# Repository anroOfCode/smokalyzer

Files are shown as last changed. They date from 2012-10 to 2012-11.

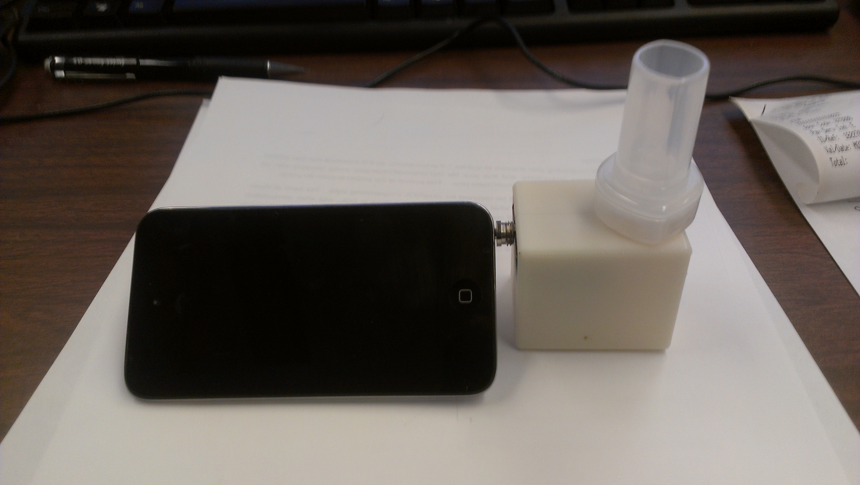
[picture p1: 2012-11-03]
photos/2012-10-05 15.16.02.jpg

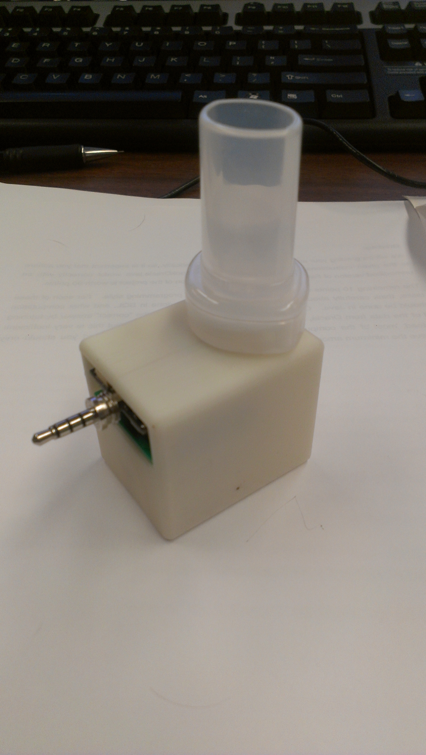
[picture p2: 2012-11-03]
photos/2012-10-05 15.00.42.jpg

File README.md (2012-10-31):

smokalyzer
==========
Code and design files for a headset-connected device that can detect if you've been smoking.

Info
====
This project is based on the HiJack platform. It includes an interface board designed for use with an electrochemical gas sensor, 3D design files for the creation of an enclosure, and code for iOS and for the HiJack platform that allows for reading and calibration.

What You'll Find Here
=====================

Code for Use With TinyOS
------------------------
Code has been written to be used with the HiJack platform, installed with TinyOS. TinyOS is difficult to setup, but the process should look something like this:

- Check out version 2.1.1 from the TinyOS Subversion page
- Install it on your local machine, including tos-tools. (see documentation on their site)
- Check out the hijack-main code from the google code project and copy the directory structure such that it matches up with your tinyos main folder
- Build the apps using 'make hijack install miniprog bsl,/dev/ttyUSB0'

An iOS App That Displays CO Data
--------------------------------
This is one of my very, very first endeavors into iOS app making. The code is not clean but will hopefully be cleaned up over time. We've imported libHiJack from the HiJack project as well, which requires delicacy when it comes to using ARC. The app supports basic calibration and reading of the instrument. 

Board Design Files
------------------
The files will allow you to order more of the PCB. They have been produced using Eagle 6.3.0.

Enclosure Design Files
----------------------
These files can serve as a starting point for a professional enclosure. They can also be 3D prototyped by any 3D lab for prototype enclosures. 

Questions?
==========
Feel free to contact me with questions. Responses are not guaranteed.

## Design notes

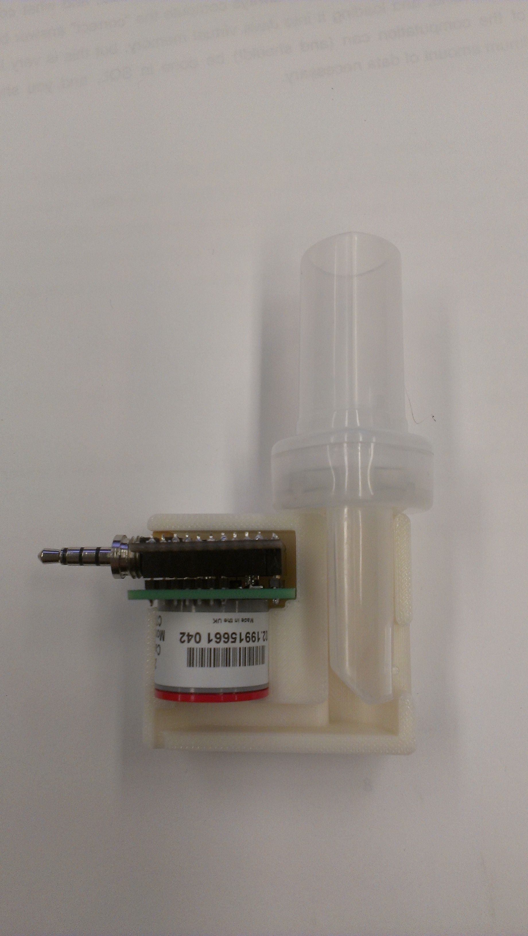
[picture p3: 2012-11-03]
photos/2012-10-05 15.00.01.jpg

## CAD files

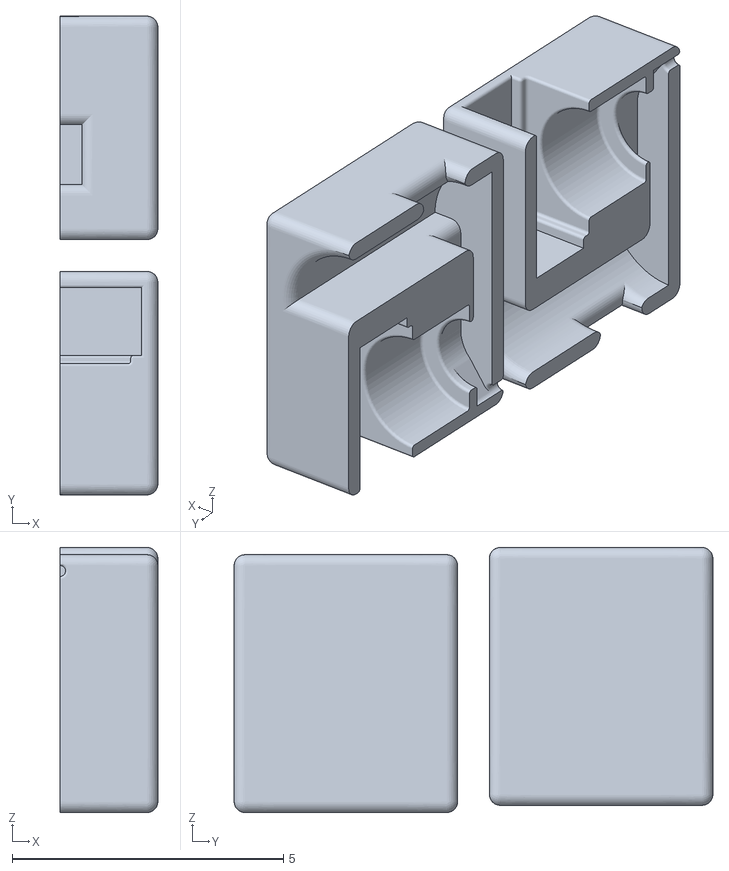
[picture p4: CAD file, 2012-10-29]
enclosure/printingLayout.stl
1.80 x 8.82 x 4.88

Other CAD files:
enclosure/design.ipt
enclosure/design_MIR.ipt
enclosure/printingLayout.iam

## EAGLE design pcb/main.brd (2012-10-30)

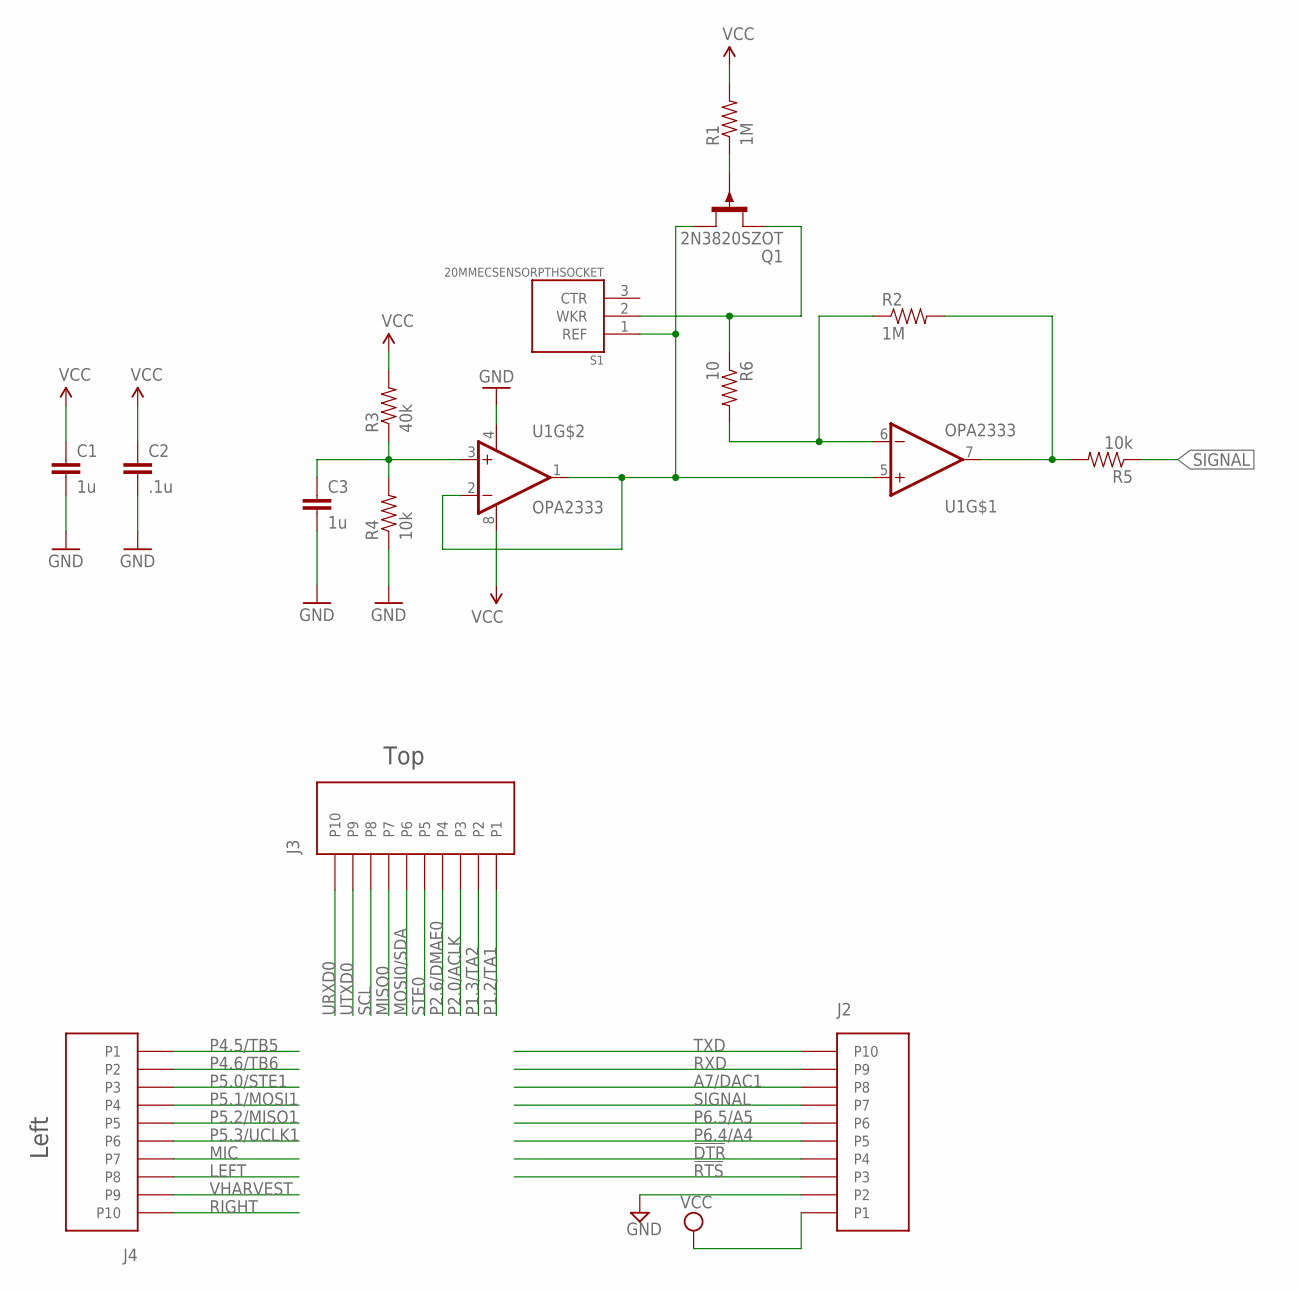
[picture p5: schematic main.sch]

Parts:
C1, C3: 1u; 0603-CAP
C2: .1u; 0603-CAP
J2, J3, J4: HEADER10POS; 10PIN2MMHEADER
Q1: 2N3820SZOT; SOT23-3
R1, R2: 1M; 0603-RES
R3: 40k; 0603-RES
R4, R5: 10k; 0603-RES
R6: 10; 0603-RES
S1: 20MMECSENSORPTHSOCKET; 20MMSENSOR
U1: OPA2333; SOIC

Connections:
!DTR: J2.P4
!RTS: J2.P3
A7/DAC1: J2.P8
GND: C1.2, C2.2, C3.2, J2.P2, R4.1, U1.4 (V-)
LEFT: J4.P8
MIC: J4.P7
MISO0: J3.P7
MOSI0/SDA: J3.P6
unnamed: Q1.1 (D), R6.1, S1.2 (WKR)
unnamed: R2.2, R5.2, U1.7 (OUT)
unnamed: R2.1, R6.2, U1.6 (-IN)
unnamed: Q1.3 (G), R1.1
P1.2/TA1: J3.P1
P1.3/TA2: J3.P2
P2.0/ACLK: J3.P3
P2.6/DMAE0: J3.P4
P4.5/TB5: J4.P1
P4.6/TB6: J4.P2
P5.0/STE1: J4.P3
P5.1/MOSI1: J4.P4
P5.2/MISO1: J4.P5
P5.3/UCLK1: J4.P6
P6.4/A4: J2.P5
P6.5/A5: J2.P6
RIGHT: J4.P10
RXD: J2.P9
SCL: J3.P8
SIGNAL: J2.P7, R5.1
STE0: J3.P5
TXD: J2.P10
URXD0: J3.P10
UTXD0: J3.P9
VCC: C1.1, C2.1, J2.P1, R1.2, R3.2, U1.8 (V+)
VHARVEST: J4.P9
VREF: Q1.2 (S), S1.1 (REF), U1.1 (OUT), U1.2 (-IN), U1.5 (+IN)
WHATEV: C3.1, R3.1, R4.2, U1.3 (+IN)

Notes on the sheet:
Left
Top

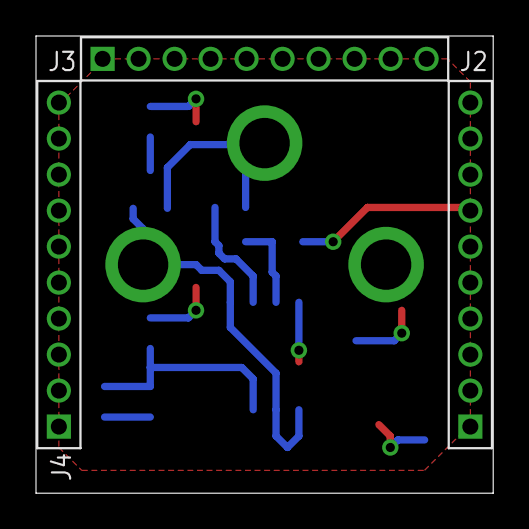
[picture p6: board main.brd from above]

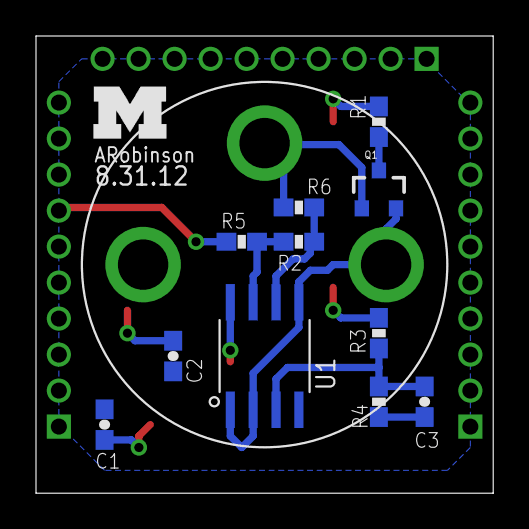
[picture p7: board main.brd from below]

Board: 2 copper layers, 25.4 x 25.4 mm, 16 parts (12 on the bottom side), 9 nets.

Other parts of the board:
U$1: BLOCK-M

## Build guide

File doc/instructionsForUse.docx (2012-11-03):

# Instructions for Using the SMOKALYZER

# Measuring

To measure simply run the Smokalzyer iPhone app, which should have come preinstalled. It will immediately start displaying readings from the unit. Upon start up the readings might take a few seconds to settle on a value around 0. Once they have done so, reset the max and perform a breath measurement.

You should try to discover a procedure that works best for you, however Bedfont’s Pico Smokeralyzer’s procedure is a good starting point. This procedure requires the subject take a deep breath in, hold it for 20 seconds, and then slowly exhale into the unit.

Breathing excessively fast (blowing) into the unit can cause the measurements to be skewed.

# Calibrating

The unit should periodically be calibrated and checked for accuracy. The sensors should show very little drift, however since this is prototype hardware we recommend frequent calibration and verification. Calibration occurs in two stages.

## Zero Calibration

Simply take the unit somewhere with fresh air and let it settle to a stable value. Press the 0 calibration button.

## 20ppm Calibration

You will need 20ppm CO calibration gas. Apply the gas to the instrument using the calibration adapter. Turn the gas on and allow the unit to reach a stable value. Press the 20ppm calibration button.

# Supplies

The units use a replaceable breathing tube which is compatible with Bedfont’s D-Piece. The tube is good for hundreds of tests, and it is suggested that it should be replaced every 30 days. Additionally a periodic calibration should be performed. The sensor inside the device is designed to last 2-3 years, at which time it should be replaced.

## D-Piece

The D-Piece should be replaced every 30 days.

http://www.covita.net/shop/index.php/accessories/d-piece.html

## Calibration Kit

The unit should be calibrated every 30 days and periodically checked for accuracy.

http://www.covita.net/shop/index.php/accessories/20-ppm-carbon-monoxide-calibration-kit.html

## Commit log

2012-10-29 Added enclosure design files.
    [design.ipt, design_MIR.ipt, printingLayout.iam, printingLayout.stl]
2012-10-30 Added internal flash storage stuff and the Makefile. Internal flash writing is currently not working.
2012-10-30 wrote test code to write device EEPROM and made interface for iOS app.
2012-10-30 working eeprom storage of calibration data
2012-10-30 fixed thread synchronization problem. working iOS app now
2012-10-30 Added pcb design files to project.
    [main.brd, main.sch]
